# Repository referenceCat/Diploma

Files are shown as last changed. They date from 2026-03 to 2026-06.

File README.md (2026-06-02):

# Средства пользовательского ввода для лабораторного макета микроконтроллера

Выпускная квалификационная работа бакалавра

Студент: М.Ю. Буянов

Руководитель: к.т.н. П.Н. Бондаренко

Консультанты: А.А. Трусов, М.Н. Гречухин

# РЕФЕРАТ

МИКРОКОНТРОЛЛЕР, MIK32 АМУР, ЛАБОРАТОРНЫЙ МАКЕТ, ПОЛЬЗОВАТЕЛЬСКИЙ ВВОД, GPIO, ДРЕБЕЗГ КОНТАКТОВ, ПРОГРАММНАЯ ОБРАБОТКА СИГНАЛОВ.

В выпускной квалификационной работе рассматриваются аппаратные и программные средства пользовательского ввода, предназначенные для применения в учебном лабораторном макете на базе микроконтроллера MIK32 АМУР. Проводится анализ существующих отладочных плат и лабораторных стендов, формулируются требования к модулю ввода и обосновывается необходимость разработки отдельной платы с набором основных органов управления.

В работе разработаны схемотехнические и программные решения решения для подключения средств пользовательского ввода.

Результат работы - плата пользовательского ввода и программные примеры, которые могут использоваться при выполнении лабораторных работ по предмету “Микропроцессорные системы.”

# ABSTRACT

In the graduation work, hardware and software user input tools intended for use in an educational laboratory prototype based on the MIK32 AMUR microcontroller are considered. Existing development boards and laboratory stands are analyzed, requirements for the input module are formulated, and the need to develop a separate board with a set of basic controls is substantiated.

The work presents circuit and software solutions for connecting user input devices.

The result of the work is a user input board and software examples that can be used in laboratory assignments for the course “Microprocessor Systems.”

# СОДЕРЖАНИЕ

# ОПРЕДЕЛЕНИЯ, ОБОЗНАЧЕНИЯ И СОКРАЩЕНИЯ

CLK — тактовый сигнал, задающий моменты передачи данных в последовательном интерфейсе.

CS — сигнал выбора микросхемы или ведомого устройства на шине SPI.

GPIO — General Purpose Input/Output, — универсальные цифровые выводы ввода-вывода микроконтроллера.

I2C — последовательный двухпроводный интерфейс обмена данными между цифровыми устройствами.

JTAG — Joint Test Action Group, — интерфейс, применяемый для отладки и программирования микроконтроллеров.

MIK32 АМУР — отечественный 32-х битный МК от фирмы Микрон, построенный на архитектуре RISC-V.

MISO — линия интерфейса SPI, по которой ведомое устройство передает данные ведущему.

RC-цепь — электрическая цепь, состоящая из резистора и конденсатора и применяемая, в том числе, для сглаживания быстрых изменений сигнала.

RISC-V — открытая архитектура набора команд процессора.

SPI — Serial Peripheral Interface, — последовательный синхронный интерфейс обмена данными.

UART — Universal Asynchronous Receiver/Transmitter, — универсальный асинхронный приемопередатчик для последовательного обмена данными.

АЦП — аналого-цифровой преобразователь, периферийный блок МК, преобразующий входное аналоговое напряжение в цифровой код.

Лабораторный макет — учебное устройство или набор узлов, предназначенный для практического изучения работы микроконтроллера и его периферийных блоков.

МК — микроконтроллер, программируемая интегральная схема, содержащая процессорное ядро, память и периферийные блоки для управления внешними устройствами.

МКС — микроконтроллерная система.

Отладочная плата — плата с микроконтроллером, разъемами, цепями питания и средствами загрузки программы, предназначенная для разработки и проверки программного обеспечения.

ПО — программное обеспечение.

Пользовательский ввод — сигналы, формируемые человеком с помощью органов управления и передаваемые в МКС.

# ВВЕДЕНИЕ

Микроконтроллеры применяются в измерительной технике, промышленной автоматике, бытовых устройствах и средствах связи. При их изучении важно связывать программную часть с реальными электрическими сигналами. Студент должен не только написать программу, но и понять, как микроконтроллер взаимодействует с кнопками, датчиками, индикаторами и другими устройствами. Лабораторный макет дает для этого наглядную и воспроизводимую среду: позволяет подать входной сигнал, проверить его обработку программой и оценить работу периферийных блоков микроконтроллера.

Целевой платформой разрабатываемого лабораторного макета является отечественный МК MIK32 АМУР. Он построен на архитектуре RISC-V и может использоваться для разработки современных встраиваемых систем [1]. Для MIK32 доступны отладочные платы, однако готовых лабораторных макетов с развитым набором органов пользовательского ввода нет, а существующие примеры программного обеспечения охватывают не все распространенные сценарии.

Данная работа посвящена разработке средств пользовательского ввода как одной из частей лабораторного макета на базе MIK32 АМУР. Остальные узлы макета разрабатываются отдельно и будут объединены с модулем ввода в общем устройстве.

В настоящее время существует небольшое количество отладочных плат для MIK32, но все они содержат только минимальный набор встроенных органов управления, например одну или две кнопки и несколько светодиодов. Для выполнения лабораторных работ требуется подключать дополнительные модули и собирать схемы на макетной плате. Это увеличивает время подготовки, повышает вероятность ошибок подключения, способных привести к повреждению МК, и затрудняет повторяемость экспериментов, поэтому разработка средств пользовательского ввода для лабораторного макета на базе MIK32 АМУР является актуальной задачей.

Целью данной работы является разработка средств пользовательского ввода для лабораторного макета МК MIK32 АМУР.

# 1 Анализ существующих лабораторных макетов и постановка требований

Данный раздел посвящен постановке требований к блоку пользовательского ввода лабораторного макета. Рассматривается роль пользовательского ввода в учебных МКС, приводится классификация устройств ввода и формулируются требования к лабораторному макету. Далее анализируются особенности применения MIK32 АМУР, доступные отладочные платы на его основе, распространенные платы на других микроконтроллерах и готовые учебные стенды. По результатам сравнения обосновывается актуальность разработки собственного модуля ввода.

## 1.1 Роль лабораторного макета в обучении работе с МКС

Лабораторные макеты микроконтроллеров применяются для изучения принципов работы цифровых устройств, периферийных модулей и программного обеспечения встраиваемых систем. Лабораторный макет отличается от законченного устройства тем, что он предназначен не для выполнения заданной функции, а для изучения процессов, происходящих в схеме и программе. Поэтому учебный макет должен быть наглядным, иметь простую для понимания электрическую схему, обеспечивать доступ к основным сигналам и позволять изменять отдельные подключения.

Средства пользовательского ввода в таком макете выполняют несколько задач:

1. Формирование команд управления программой.

2. Задание режимов работы устройства.

3. Имитация внешних дискретных и аналоговых сигналов.

4. Отладка алгоритмов обработки событий пользователя.

К средствам ввода относятся кнопки, переключатели, потенциометры и различные датчики. Эти устройства позволяют микроконтроллеру получать информацию об окружающем мире.

При разработке необходимо учитывать не только удобство пользователя, но и ограничения аппаратной платформы. Модуль не должен занимать слишком много выводов микроконтроллера, обработка входных сигналов не должна занимать слишком много памяти и процессорного времени МК.

## 1.2 Классификация устройств пользовательского ввода

Устройства пользовательского ввода можно классифицировать по характеру формируемого сигнала и способу его обработки микроконтроллером. В микроконтроллерных системах наиболее распространены дискретные, аналоговые, импульсные. Также можно выделить интерфейсные устройства ввода — это устройства, которые относятся к первым 3 группам, но взаимодействуют с МК через один из популярных протоколов связи, например UART, I2C, SPI, а не напрямую. В учебном макете целесообразно использовать простые представители этих групп, так как они позволяют изучить базовые принципы обработки сигналов без лишней схемотехнической сложности.

Дискретные устройства формируют один из двух логических уровней. К ним относятся кнопки, переключатели, тумблеры, концевые выключатели, герконы и датчики с дискретным выходом. Было решено использовать в макете тактовые кнопки и рычажковые переключатели: кнопка формирует кратковременное событие, а переключатель задает устойчивое состояние. На этих элементах можно изучить считывание GPIO, обработку изменения уровня и подавление дребезга контактов. Рассматривалась возможность использовать группу штыревых разъемов с джампером, так как они надежнее переключателей, но джамперы могут легко потеряться при постоянном переключении и не так удобны в использовании.

При увеличении числа команд отдельные кнопки удобно объединять в клавиатурный блок. Если подключать каждую кнопку напрямую к отдельному выводу микроконтроллера, расход GPIO быстро становится слишком большим: например, для клавиатуры из 12 кнопок потребуется 12 входных линий без учета переключателей, энкодера и аналоговых регуляторов. Поэтому клавиатура отличается от простого набора кнопок не только конструктивным исполнением, но и способом организации считывания: несколько кнопок объединяются в общую схему и опрашиваются программно.

В работе используется клавиатура 4x3, содержащая 12 кнопок. На ее примере рассматривается задача считывания группы дискретных входов при ограниченном числе выводов микроконтроллера. Такая клавиатура может подключаться напрямую, матрицей строк и столбцов или через внешние регистры ввода. Сравнение этих вариантов позволяет выбрать схему, которая обеспечивает достаточное количество команд и при этом не занимает чрезмерное число GPIO.

Аналоговые устройства ввода формируют непрерывно изменяющееся напряжение, которое измеряется АЦП. К ним относятся потенциометры, аналоговые джойстики и датчики с аналоговым выходом. В работе в качестве базового аналогового элемента используется потенциометр, поскольку это одно из наиболее простых и понятных аналоговых устройств ввода.

Импульсные устройства ввода формируют последовательность переходов между логическими уровнями. К ним относятся механические, оптические и магнитные энкодеры, а также датчики с импульсным или квадратурным выходом. В работе используется механический поворотный энкодер. При его вращении формируются два связанных сигнала, по которым программа определяет направление и количество шагов. Такой элемент позволяет изучить обработку переходов, измерение временных характеристик сигнала и влияние частоты опроса на корректность распознавания.

Отдельную группу составляют интерфейсные устройства ввода, которые передают данные по SPI, I2C, UART или USB. К ним относятся клавиатурные контроллеры, сенсорные панели, цифровые джойстики, RFID-считыватели и датчики с цифровым выходом. Для учебного макета удобным примером является клавиатура с внешним контроллером или регистром ввода: ее состояние задается пользователем и легко проверяется визуально, поэтому обмен по цифровому интерфейсу можно изучать без дополнительного контроля внешней физической величины.

В данной работе основной акцент сделан на простых и наглядных устройствах ввода: кнопках, переключателях, клавиатуре, потенциометрах и поворотном энкодере. Такой выбор позволяет изучить основные типы сигналов, с которыми сталкивается микроконтроллер: логический уровень, аналоговое напряжение и импульсную последовательность. После освоения этих базовых случаев можно переходить к более сложным устройствам, так как они в большинстве случаев используют те же принципы.

## 1.3 Требования к лабораторному макету пользовательского ввода

Лабораторный макет пользовательского ввода должен быть пригоден для регулярного применения в учебном процессе. Поэтому к нему предъявляются требования, связанные с составом устройств, стоимостью, удобством эксплуатации, использованием ресурсов микроконтроллера и возможностью расширения.

Основные требования к такому макету можно сформулировать следующим образом:

Наличие основных типов устройств ввода. Макет должен содержать дискретные органы управления, аналоговые устройства, импульсное устройство ввода и интерфейсное устройство. Такой состав позволяет выполнять лабораторные работы по всем базовым видам пользовательского ввода. Навыки полученные в ходе выполнения ЛР позволят студентам работать с устройствами которые не представлены на макете.

Умеренная стоимость. Учебный макет должен быть доступен для изготовления в нескольких экземплярах, так как лабораторное оборудование обычно используется не одним студентом, а учебной группой.

Доступность элементной базы. При разработке необходимо использовать распространенные компоненты и избегать избыточно сложных узлов, если их функции можно показать на более простых элементах. Это упрощает изготовление, ремонт и повторение макета.

Экономное использование выводов микроконтроллера. В лабораторном макете выводы GPIO нужны не только для пользовательского ввода, но и для интерфейсов связи, отладки, индикации, измерений и подключения внешних модулей.

Удобство наблюдения и проверки сигналов. Основные линии ввода желательно вывести на контактные площадки или разъемы, к которым можно подключить осциллограф, логический анализатор или мультиметр.

Эргономика. Органы управления должны быть расположены так, чтобы студент мог быстро понять их назначение. Кнопки, переключатели, энкодер и аналоговые ручки должны иметь понятные обозначения, а их состояние должно легко считываться визуально.

Ремонтопригодность. В учебных условиях отдельные элементы могут выходить из строя из-за интенсивного использования, поэтому предпочтительно применять доступные компоненты и разборные соединения. Это позволяет заменить поврежденный элемент без переработки всей платы.

Таким образом, хороший лабораторный макет пользовательского ввода должен сочетать достаточный набор органов управления, низкую стоимость, экономное использование выводов, удобство измерений, надежность и понятную компоновку. Эти требования используются далее при анализе существующих плат и при разработке собственного модуля ввода.

## 1.4 MIK32 АМУР как целевая платформа учебного макета

В данной работе микроконтроллер MIK32 АМУР задан в качестве целевой аппаратной платформы лабораторного макета. Согласно техническому описанию, MIK32 АМУР является 32-разрядным микроконтроллером на архитектуре RISC-V [1].

На момент выполнения работы микроконтроллер доступен в 64-выводном корпусе QFN [2]. Часть выводов используется для питания, тактирования, отладки и интерфейсов связи, поэтому число линий, доступных для органов пользовательского ввода составляет 40 [1], поэтому при разработке макета необходимо экономно расходовать GPIO и предусматривать способы сокращения числа занятых выводов.

Схема ввода должна быть согласована с электрическими параметрами MIK32. Согласно информационному листу, напряжение питания микроконтроллера составляет 3,3 В ±10 % [2]. Цифровые устройства ввода должны формировать уровни, допустимые для входов микроконтроллера. Для аналоговых входов дополнительно учитывается диапазон входного сигнала АЦП: согласно техническому описанию, он составляет 0,015...Uref, где Uref находится в пределах 1,1...1,3 В и имеет номинальное значение 1,2 В [1]. Поэтому сигналы от потенциометров и других аналоговых источников должны быть ограничены до допустимого диапазона АЦП.

Для MIK32 доступно меньше готовых примеров программ, чем для более распространенных платформ, таких как Arduino или STM32. В частности, готовых примеров работы со сдвиговыми регистрами 74HC165 и поворотным энкодером для MIK32 найти не удалось. Поэтому программные алгоритмы опроса, фильтрации и преобразования входных состояний необходимо разрабатывать и проверять самостоятельно.

## 1.5 Обзор доступных отладочных плат на базе MIK32

На момент выполнения работы доступны несколько отладочных плат и модулей на базе MIK32. Они позволяют познакомиться с микроконтроллером, загрузить программу и подключить внешние устройства, однако их возможности с точки зрения готового пользовательского ввода ограничены.

DIP-MIK32 представляет собой компактный модуль с микроконтроллером MIK32, разъемами и минимальной необходимой обвязкой [4]. Такое исполнение удобно для прототипирования и установки на макетную плату. Однако развитых средств пользовательского ввода на нем нет: для выполнения лабораторных работ требуется собирать дополнительную схему. Стоимость DIP-MIK32 на странице заказа АО «Микрон» составляет 5 500 руб. [4]. Внешний вид платы представлен на рисунке 1.1.

Плата СТАРТ-MIK32 является более готовым решением для запуска программ, так как содержит внешнюю flash-память и программатор [4, 5]. Это облегчает первое знакомство с микроконтроллером и снижает порог входа при отладке программ. Тем не менее, с точки зрения лабораторных работ по пользовательскому вводу ее возможности также ограничены. Стоимость платы на странице заказа составляет 7 500 руб. [4].

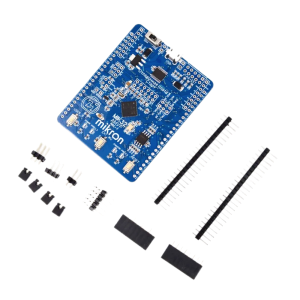
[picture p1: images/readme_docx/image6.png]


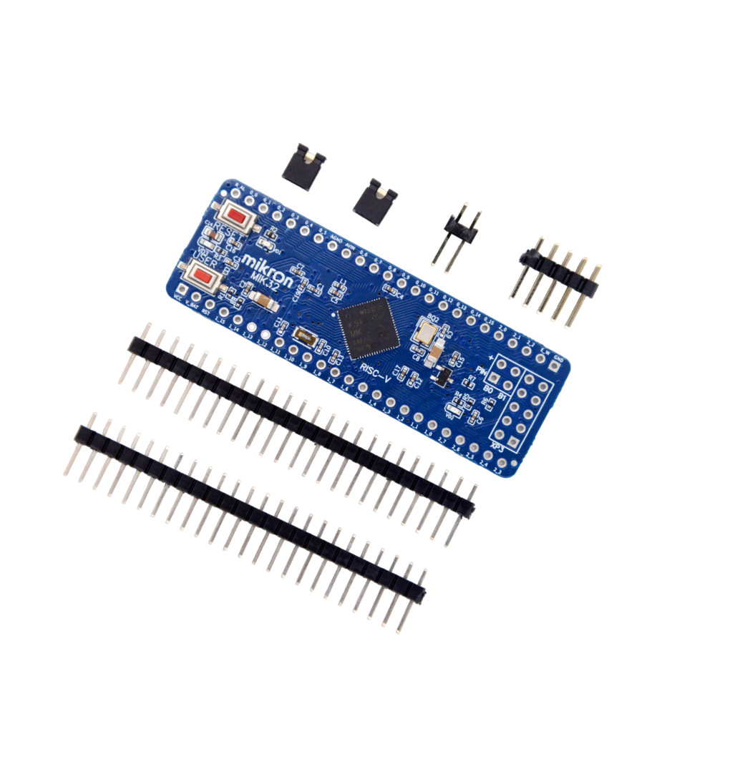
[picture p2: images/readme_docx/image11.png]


###### Рисунок 1.1 — Отладочные платы производства АО «Микрон» СТАРТ-MIK32 (слева) и DIP-MIK32 (справа)

Плата ELBEAR ACE-UNO выполнена в форм-факторе, близком к Arduino UNO, и может использоваться с Arduino-совместимыми модулями расширения [6]. Это делает ее удобной для экспериментов, так как многие периферийные устройства можно подключать через стандартные разъемы. Однако встроенных средств ввода на самой плате немного: пользовательская кнопка и светодиод. Стоимость платы в интернет-магазине Arduino54 составляет 8 400 руб. [6]. Внешний вид платы представлен на рисунке 1.2.

Плата RADIANT MIK32 также ориентирована на разработку и эксперименты с MIK32. В ее руководстве указаны пользовательские кнопки, светодиоды, Arduino UNO-совместимый разъем и выводы GPIO [7]. Это решение ближе к учебной отладочной плате, чем минимальные модули, однако и оно не содержит развитого набора органов управления. Для большинства лабораторных работ по пользовательскому вводу все равно потребуется отдельный модуль или внешняя макетная сборка. Стоимость составляет 9 060 руб. [7].

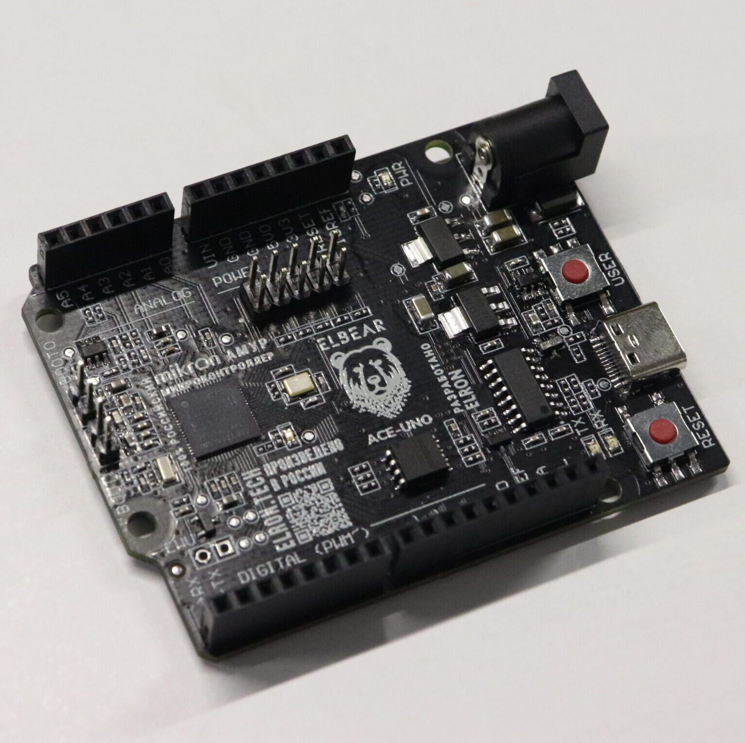
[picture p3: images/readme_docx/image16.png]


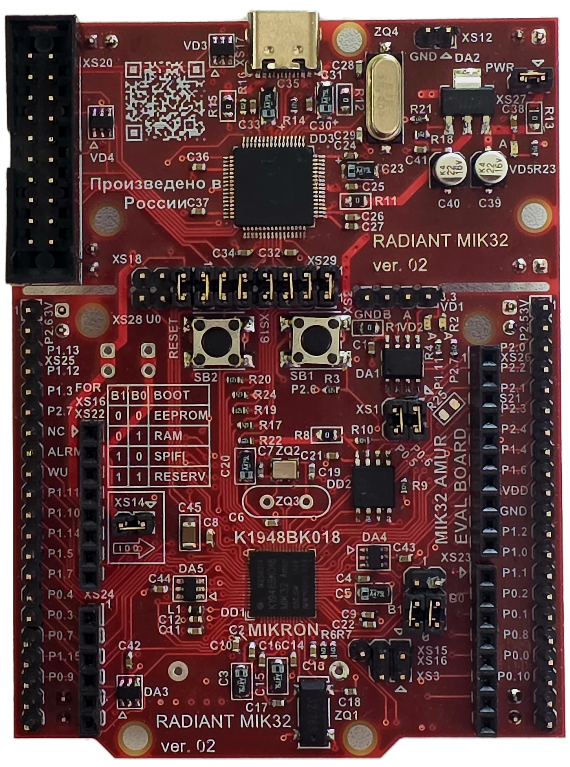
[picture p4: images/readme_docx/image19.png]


###### Рисунок 1.2 — Отладочные платы сторонних производителей ELBEAR ACE-UNO (слева) и RADIANT MIK32 (справа)

Следовательно, доступные платы на базе MIK32 решают задачу запуска и отладки программ, но не закрывают задачу готового лабораторного макета пользовательского ввода. Они предоставляют микроконтроллер и интерфейсы подключения, однако набор встроенных органов управления слишком мал для системного изучения устройств ввода. Одну из рассмотренных плат можно использовать как часть лабораторного макета. В этом случае не потребуется заново разрабатывать программатор, схему питания и минимальную обвязку микроконтроллера.

## 1.6 Сравнение с платами на других микроконтроллерах

Для оценки ситуации полезно сравнить платы MIK32 с распространенными решениями на других МК. Такие платы широко используются в обучении и прототипировании, поэтому они позволяют понять, какие подходы уже применяются в учебной практике.

Одним из самых дешевых решений является STM32F103C8T6 Blue Pill, изображенная на рисунке 1.3. Эта отладочная плата имеет большое количество выведенных контактов ввода-вывода и низкую стоимость: на странице магазина Амперо указана цена 249-299 руб. [8]. При этом встроенных средств пользовательского ввода на плате нет.

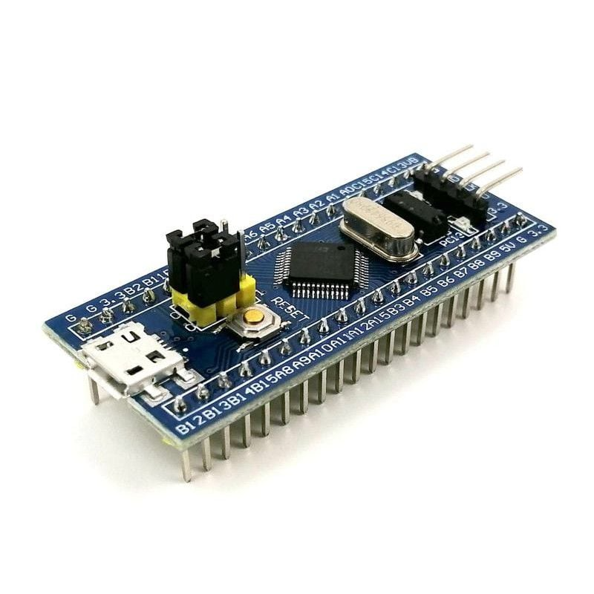
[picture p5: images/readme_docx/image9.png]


###### Рисунок 1.3 — Отладочная плата STM32F103C8T6 Blue Pill

Более удачным примером с точки зрения комплектации является Arduino Student Kit (рисунок 1.4). В него входит плата Arduino UNO, макетная плата, кнопки, потенциометры и другие компоненты для выполнения учебных заданий [9]. По составу комплект хорошо подходит для обучения, так как содержит не только микроконтроллерную плату, но и набор периферийных элементов. Однако схемы в нем необходимо каждый раз собирать на макетной плате.

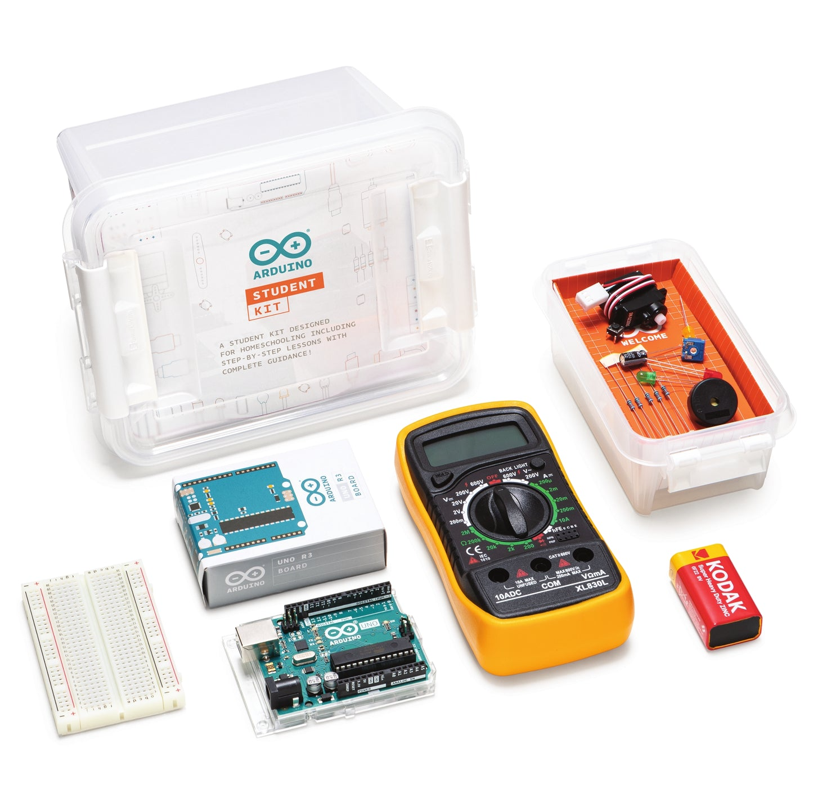
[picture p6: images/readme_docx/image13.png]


###### Рисунок 1.4 — Набор Arduino Student Kit

Хорошим примером завершенного учебного решения является MIKROE-701 UNI DS6 Development System. На странице поставщика она описана как универсальная отладочная плата, или лабораторный стенд, для изучения микроконтроллеров разных архитектур [10]. Плата содержит большое количество устройств ввода и вывода, гибкую систему коммутации, 12-разрядный внешний АЦП, температурный датчик, USB-UART мосты и разъемы для подключения внешних плат расширения. Цена платы на момент написания работы составляет 13 780 руб, что сопоставимо с ценой отладочных плат для MIK32. Такое решение хорошо показывает, каким должен быть учебный макет: студент получает готовую среду для экспериментов, а не набор отдельных элементов. При этом стенд не ориентирован на MIK32 и не может быть напрямую использован как решение задачи данной работы. Плата изображена на рисунке 1.5.

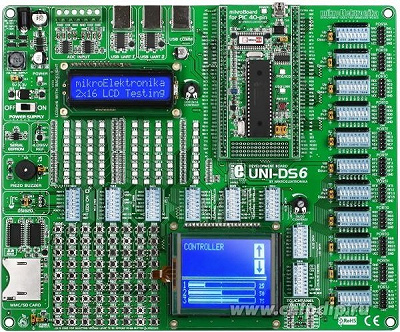
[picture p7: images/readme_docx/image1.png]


###### Рисунок 1.5 — MIKROE-701 UNI DS6

## 1.7 Сравнение с готовыми учебными лабораторными стендами

Отдельную группу решений составляют профессиональные учебные стенды для изучения микроконтроллеров. В отличие от обычных отладочных плат, такие стенды часто содержат набор тумблеров, кнопок, индикаторов, аналоговых датчиков, разъемов, клемм и методических материалов. Например, лабораторный стенд ЭЛБ-020.003.03 предназначен для изучения программирования микроконтроллеров и содержит элементы, необходимые для выполнения учебных работ [11], представлен на рисунке 1.6.

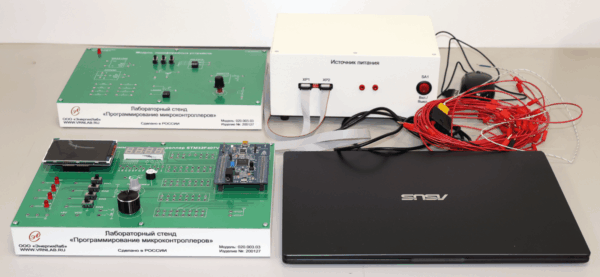
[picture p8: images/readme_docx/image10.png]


###### Рисунок 1.6 — Лабораторный стенд «Программирование микроконтроллеров» ЭЛБ-020.003.03

Преимущество таких стендов заключается в их завершенности. Студент работает с готовым оборудованием, где органы управления, индикация и измерительные точки уже размещены на панели и согласованы с учебной методикой. Это снижает количество ошибок подключения и делает лабораторные занятия более повторяемыми.

Основным недостатком готовых стендов является высокая стоимость. Например, цена стенда ЭЛБ-020.003.03 на странице поставщика составляет 392 824 руб. [11]. Такая стоимость существенно превышает стоимость большинства отладочных плат и делает стенд труднодоступным для небольших лабораторий, индивидуальной разработки и тиражирования в учебных группах. Кроме того, подобные стенды ориентированы на другие микроконтроллеры, например AVR или STM32, и не предназначены для работы с MIK32.

## 1.8 Сравнительный анализ решений

Сводное сравнение рассмотренных решений с точки зрения наличия различных устройств ввода приведено в таблице 1.1. В таблице указаны контроллеры, состав средств ввода, ориентировочная стоимость и вывод о применимости решения для задач данной работы. Стоимость приведена по открытым источникам на дату обращения и используется как ориентир для сравнения классов устройств.

Таблица 1.1 — Сравнение отладочных плат и лабораторных макетов

| Решение | Контроллер | Средства ввода | Ориентировочная стоимость | Вывод |
| --- | --- | --- | --- | --- |
| DIP-MIK32 | MIK32 АМУР | нет | 5 500 руб. [4] | Требуется внешний модуль ввода |
| СТАРТ-MIK32 | MIK32 АМУР | 1 кнопка | 7 500 руб. [4] | Требуется внешний модуль ввода |
| ELBEAR ACE-UNO | MIK32 АМУР | 1 кнопка | 8 400 руб. [6] | Требуется внешний модуль ввода |
| RADIANT MIK32 | MIK32 АМУР | 2 кнопки | 9 060 руб. [7] | Требуется внешний модуль ввода |
| Blue Pill | STM32F103 | нет | 249-299 руб. [8] | TI EK-TM4C123GXL LaunchPad |
| Arduino Student Kit | ATmega328P | 5 кнопок, 2 потенциометра 10 кОм, набор популярных датчиков | $79.75 [9], около 6000 руб. | Хорошая комплектация, но схемы нужно собирать |
| MIKROE-701 UNI DS6 | PIC, AVR, 8051, ARM, PSoC, dsPIC | десятки кнопок и рычажковых переключателей, внешний АЦП, датчик температуры | 13 780 руб. [10] | Хороший пример лабораторного макета, но не на MIK32 |
| ЭЛБ-020.003.03 | AVR | 8 тумблеров, 2 кнопки, внешний АЦП | 392 824 руб. [11] | Достаточный функционал, но очень высокая стоимость |

Из таблицы видно, что платы на базе MIK32 находятся в ценовом диапазоне, приемлемом для отладочных средств, однако они не содержат развитого набора пользовательского ввода. Платы на других микроконтроллерах демонстрируют ту же особенность: они удобны для программирования и подключения внешних модулей, но штатных кнопок, переключателей и аналоговых органов управления у них мало. Учебные комплекты и профессиональные стенды лучше подходят для лабораторной работы, однако они либо построены на другой аппаратной платформе, либо имеют высокую стоимость.

## 1.9 Актуальность работы и постановка задачи разработки

Проведенный анализ показывает, что задача разработки лабораторного макета для MIK32 АМУР в целом и средств пользовательского ввода для него в частности является актуальной, поскольку существующие решения не закрывают ряд требований, важных для учебного применения.

На рынке отсутствует доступный и функционально полный учебный макет на базе MIK32, ориентированный именно на изучение пользовательского ввода. Существующие платы позволяют познакомиться с микроконтроллером, но не предоставляют достаточного набора органов управления для проведения полноценных лабораторных работ.

В доступных платах на базе MIK32 отсутствует развитый набор средств пользовательского ввода. DIP-MIK32, СТАРТ-MIK32, ELBEAR ACE-UNO и RADIANT MIK32 подходят для запуска и отладки программ, но в них мало встроенных кнопок, переключателей и аналоговых регуляторов. Для учебного макета этого недостаточно, так как студенту необходимо изучать не один отдельный вход, а несколько типов пользовательского воздействия: дискретные сигналы, клавиатурный ввод, аналоговое напряжение и импульсные сигналы энкодера.

Сравнение с другими платами и стендами показывает разрыв между дешевыми отладочными платами и дорогими профессиональными учебными стендами. Недорогие платы имеют мало встроенных средств ввода, а функционально богатые стенды стоят значительно дороже. Решение на подобие MIKROE-701 UNI DS6 будет оптимальным с точки зрения соотношения цены и практичности.

Для MIK32 доступно меньше готовых примеров программ, чем для более распространенных платформ, таких как Arduino или STM32. Это означает, что для лабораторного макета недостаточно разработать только аппаратную часть. Необходимо также подготовить алгоритмы опроса кнопок и переключателей, обработки клавиатуры, определения направления вращения энкодера и считывания аналоговых значений. Без такой программной части макет будет менее полезен в учебном процессе.

Таким образом, актуальность работы определяется тем, что в существующих продуктах отсутствует сочетание свойств, необходимых для учебного макета на базе MIK32: отечественный микроконтроллер, развитый набор устройств пользовательского ввода, умеренная стоимость, возможность отключения отдельных блоков, удобство измерений и наличие программных примеров для лабораторных работ.

В связи с этим в работе ставится задача разработки средств пользовательского ввода для лабораторного макета микроконтроллера MIK32 АМУР. Разрабатываемое решение должно включать аппаратную часть, обеспечивающую подключение кнопок, переключателей, клавиатуры, энкодера и аналоговых регуляторов, а также программные примеры для их опроса и обработки. В следующих разделах рассматриваются схемотехнические варианты подключения устройств ввода, особенности их программной обработки и проверка работоспособности разработанного решения.

# 2 Разработка дискретных средств ввода

Данный раздел посвящен разработке дискретных средств пользовательского ввода, предназначенных для формирования логических сигналов, обрабатываемых микроконтроллером. Рассматриваются требования к кнопкам и переключателям, способы подключения клавиатуры 4x3, методы расширения числа входов и алгоритмы программной обработки дискретных сигналов.

## 2.1 Требования к дискретным устройствам ввода

Дискретные устройства ввода предназначены для формирования логических сигналов, по которым программа микроконтроллера определяет действия пользователя. В разрабатываемом лабораторном макете используются два типа таких устройств: тактовые кнопки для кратковременных команд и рычажковые переключатели для задания устойчивых состояний. Для макета требуется подключить 12 кнопок, например цифры от 0 до 9, ВВОД и ОТМЕНА, которые можно рассматривать как клавиатуру 4x3, и 8 рычажковых переключателей.

Для макета принято решение использовать рычажковые переключатели как наиболее простые дискретные устройства ввода. Их состояние можно считать непосредственно из регистра GPIO без настройки внешнего интерфейса и сложной схемы опроса. Это удобно для начальных лабораторных работ, где необходимо показать связь между положением элемента управления и логическим уровнем на входе микроконтроллера.

Для большого количества кнопок используется клавиатура 4x3. В отличие от отдельных переключателей, клавиатура содержит группу однотипных кнопок, число которых в дальнейшем может быть увеличено, например при переходе к клавиатуре 4x4 или панели функциональных клавиш. Поэтому способ подключения клавиатуры должен сохранять общий принцип считывания группы кнопок и по возможности не приводить к пропорциональному росту числа занятых выводов микроконтроллера.

При выборе способа подключения необходимо учитывать временные характеристики пользовательского ввода и минимизировать расход ресурсов контроллера, в первую очередь количество занятых GPIO.

## 2.2 Временные параметры опроса кнопок и переключателей

Для определения временных параметров пользовательского воздействия была проведена серия из 10 экспериментов с быстрым нажатием кнопки и переключением переключателя. [12] В макете используются переключатели DIP Switch 2.54 mm Regular Type производства CONNFLY [13] и тактовые кнопки серии KLS7-TS6601 6x6 [14]. По результатам измерений наименьшая продолжительность нажатия составила около 40 мс, продолжительность отпускания тоже около 40 мс. Для переключателей минимальная длительность одного состояния около 300 мс.

Эти значения рассматриваются как предельные условия работы, полученные при намеренно быстром нажатии на кнопку; при обычной эксплуатации лабораторного макета такие режимы, как правило, достигаться не будут.

Длительность дребезга кнопки, использованной в макете, не превысила 1 мс и, как правило, составляла около 50 мкс, как видно на осциллограмме на рисунке 2.1. На рисунке ниже приведена осциллограмма дребезга данной модели кнопки. Для рычажковых переключателей длительность дребезга не превысила 5 мс.

Продолжительность состояния и дребезга кнопок и переключателей приведена в диаграмме на рисунке 2.2.

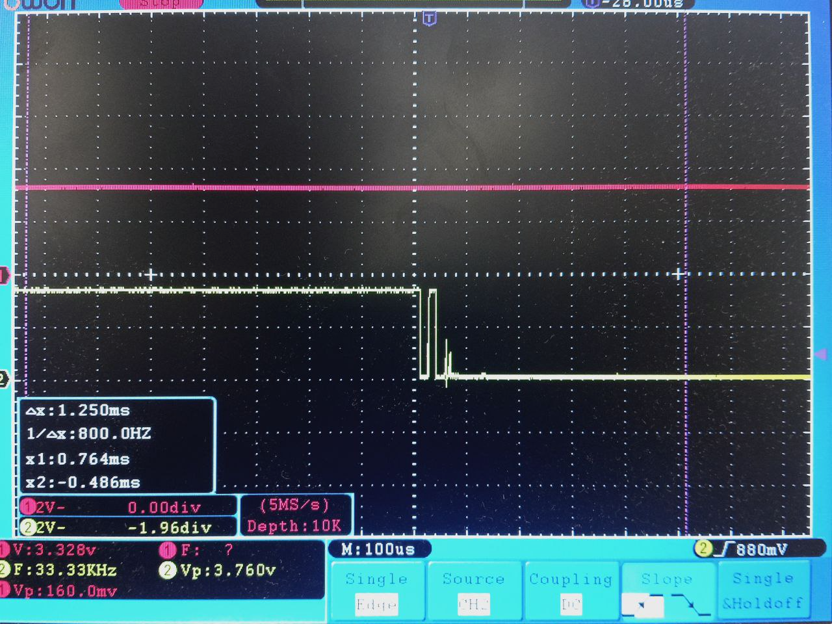
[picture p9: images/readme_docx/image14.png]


###### Рисунок 2.1 — Один из тестов длительности дребезга кнопки. Кнопка подключена ко второму каналу осциллографа

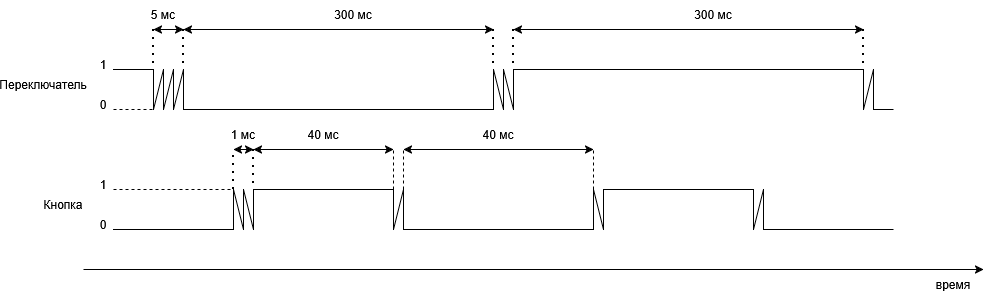
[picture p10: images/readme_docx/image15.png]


###### Рисунок 2.2 — Временные характеристики нажатия кнопки и переключателя: максимальная длительность дребезга, минимальная продолжительность состояний "0" и "1"

На основании этих измерений система опроса должна иметь запас и надежно регистрировать нажатия длительностью не менее 40 мс. Алгоритм обработки должен определять текущее состояние и его смену, подавлять дребезг контактов, при условии что будет выбран аппаратный способ борьбы с дребезгом, и сохранять возможность обработки нескольких входов в пределах одного цикла опроса. Период опроса должен быть выбран так, чтобы программа успевала обнаруживать самые быстрые действия пользователя и при этом не тратила лишние вычислительные ресурсы.

Для лабораторного макета важно сохранить компромисс между надежностью и отзывчивостью. Слишком малое время фильтрации может пропускать дребезг и приводить к ложным срабатываниям, а слишком большое - ухудшать реакцию на быстрые нажатия.

Период опроса должен быть в несколько раз меньше длительности одного состояния, например 10 мс для кнопок и 70 мс для переключателей, так в худшем случае на одно состояние придется 3 опроса. При этом итоговая задержка реакции складывается из периода опроса и выбранного времени фильтрации.

## 2.3 Подключение рычажковых переключателей

Рычажковый переключатель задает устойчивое логическое состояние, которое сохраняется после воздействия пользователя. Поэтому он подходит для выбора режима работы, задания начальных условий программы или имитации простого датчика с дискретным выходом. В разрабатываемом макете используется 8 рычажковых переключателей, подключенных напрямую к выводам GPIO микроконтроллера. Каждый переключатель остается независимым входом, поэтому его состояние можно считывать как при периодическом опросе, так и при обработке прерывания по изменению уровня.

Дискретные входы должны быть согласованы с логическими уровнями МИК32 АМУР. Согласно информационному листу микроконтроллера, напряжение питания составляет 3,3 В ±10 % [2], то есть допустимый диапазон питания основного домена составляет 2,97-3,63 В. В проектируемой схеме логический «0» должен формироваться уровнем, близким к GND, а логическая «1» - уровнем, близким к VCC 3,3 В. Подача на входы сигналов уровня 5 В не допускается.

При прямом подключении один контакт переключателя соединяется с линией питания, а второй подключается к входу микроконтроллера. Чтобы вход не оставался в неопределенном состоянии, используется подтягивающий резистор. В выбранной схеме подтяжка выполнена к земле: при разомкнутом контакте на входе формируется логический «0», а при замыкании переключателя вход соединяется с питанием и формируется логическая «1». Подтяжка реализована внешним резистором для каждого переключателя. Схема подключения представлена на рисунке 2.3.

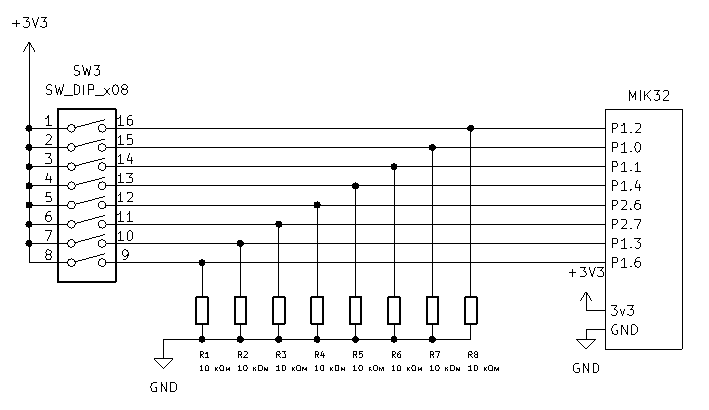
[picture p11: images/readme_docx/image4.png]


Рисунок 2.3 — Схема подключения рычажковых переключателей

Для определения состояния переключателя достаточно настроить нужный вход МК на вход и прочитать бит из соответствующего регистра. Фрагмент примера из приложения А:

GPIO_1->DIRECTION_IN = GPIO_PIN_2;

uint8_t lever_state = (GPIO_1->STATE & GPIO_PIN_2) != 0;

При изменении положения контакты переключателя не переходят из одного состояния в другое мгновенно. Как и у кнопок, у них возникает дребезг контактов, из-за которого микроконтроллер может зафиксировать несколько быстрых изменений уровня вместо одного переключения. Вопрос подавления дребезга рассматривается далее в отдельном подразделе.

## 2.4 Подключение клавиатуры 4x3 напрямую

Самый простой способ заключается в соединении каждой кнопки с отдельным входом микроконтроллера. В этом случае 12 кнопок требуют 12 GPIO. Один контакт кнопки подключается к линии питания, а второй - к входу микроконтроллера, аналогично с переключателями в подраздела 2.3. Прямое подключение клавиатуры 4x3 рассматривается как базовый вариант, с которым далее сравниваются другие способы подключения.

Преимущество прямого подключения заключается в простоте схемы и программы. Состояние каждой кнопки можно считать напрямую из регистра GPIO, а обработка нажатий сводится к сравнению текущего и предыдущего состояния входа. При таком подходе легко поддерживать одновременные нажатия, поскольку каждая кнопка имеет собственный входной канал. Кроме того, прямое подключение позволяет использовать внешние прерывания GPIO для реакции на изменение состояния кнопки без постоянного циклического опроса всех входов. Можно добавить аппаратное средство борьбы с дребезгом.

Программный код для прямого подключения клавиатуры аналогичен коду для рычажковых переключателей: для каждой кнопки настраивается вход GPIO, после чего программа считывает соответствующий бит регистра состояния порта. Отличие состоит только в количестве входов.

Недостаток прямого подключения состоит в большом расходе выводов микроконтроллера. Только клавиатура 4x3 занимает 12 GPIO, а с учетом 8 рычажковых переключателей суммарно требуется уже 20 цифровых входов, не считая энкодера, аналоговых ручек и других сигналов макета. Для лабораторного стенда выводы микроконтроллера являются одним из наиболее ценных ресурсов. Поэтому прямое подключение не является оптимальным решением для итоговой платы.

## 2.5 Подключение клавиатуры 4x3 матрицей

Матричное подключение уменьшает число занятых выводов за счет объединения кнопок в строки и столбцы. Для клавиатуры 4x3 требуется 7 линий: 4 строки и 3 столбца. При сканировании программа поочередно активирует строки и считывает состояние столбцов. Если при активной строке на одном из столбцов обнаруживается изменение уровня, программа определяет нажатую кнопку по номеру строки и столбца.

По сравнению с прямым подключением матрица позволяет сэкономить 5 выводов микроконтроллера: вместо 12 GPIO используются 7. Однако такая схема требует более сложного алгоритма опроса. Необходимо последовательно переключать строки, выдерживать время установления уровней и выполнять чтение столбцов для каждой строки. Период полного опроса клавиатуры зависит от числа строк и задержек в алгоритме сканирования. В отличие от прямого подключения, матрица не позволяет назначить независимое прерывание на каждую кнопку. Алгоритм сканирования матрицы включает несколько этапов:

Перевести одну строку в активное состояние.

Выдержать небольшую задержку для установления уровней.

Считать уровни на линиях столбцов.

Определить нажатые кнопки для текущей строки.

Повторить действия для остальных строк.

Дополнительная проблема матричной клавиатуры возникает при одновременном нажатии нескольких кнопок. В некоторых сочетаниях возможно появление фантомных срабатываний, когда программа определяет нажатой кнопку, которая фактически не нажималась. Для устранения этой проблемы применяют диоды [15], включенные последовательно с кнопками, но это увеличивает количество компонентов и усложняет монтаж: для клавиатуры 4x3 требуется 12 диодов и 3 резистора. Схема подключения клавиатуры 4х4 изображена на рисунке 2.4, для клавиатуры 4х3 схема аналогична за исключением отсутствия левого столбца кнопок.

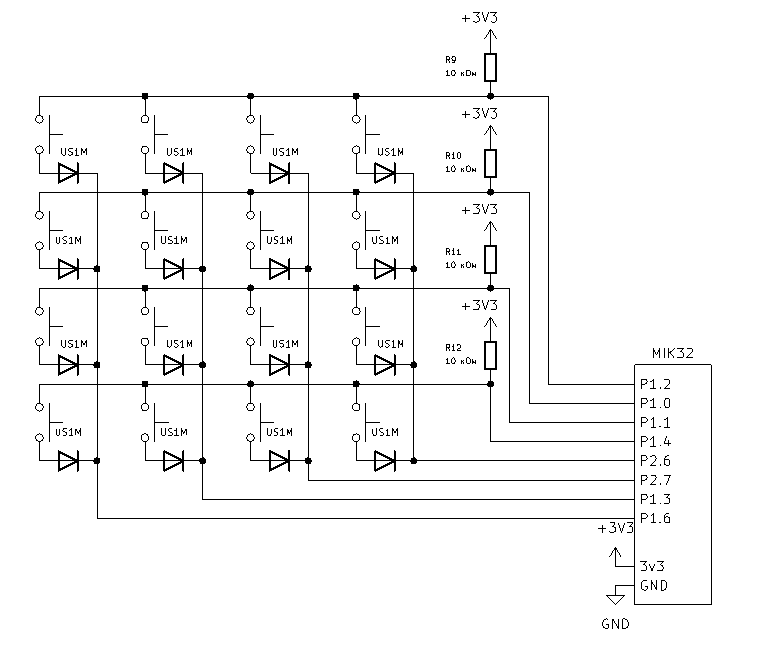
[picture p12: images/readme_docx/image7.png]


###### Рисунок 2.4 — Схема подключения клавиатуры 4 на 4

Матричное подключение экономит GPIO, но добавляет схемотехнические и усложняет ПО.

## 2.6 Подключение кнопок через сдвиговые регистры 74HC165

Третий вариант заключается в подключении кнопок к параллельным входам сдвигового регистра, например 74HC165. 74HC165 является распространенным решением: микросхема выпускается разными производителями и представлена в каталогах поставщиков в значительных количествах [16-18]. Один 74HC165 имеет 8 параллельных входов, поэтому для 12 кнопок достаточно двух микросхем. Оставшиеся входы могут быть зарезервированы для дальнейшего расширения, например для кнопки на ручке энкодера. Подключение 74HC165 занимает 3 выхода МК [12].

При работе с 74HC165 микроконтроллер сначала формирует сигнал загрузки параллельных входов, после чего последовательно считывает биты состояния. Несколько микросхем можно каскадировать: последовательный выход одной микросхемы подключается к последовательному входу следующей, и вся цепочка считывается как один более длинный сдвиговый регистр. Это делает решение хорошо расширяемым: увеличение числа кнопок требует добавления микросхемы, но почти не увеличивает число линий микроконтроллера. Недостатком такого подхода является невозможность получить отдельное прерывание от каждой кнопки: микроконтроллер видит не отдельные входы, а последовательный поток данных, поэтому состояние кнопок определяется периодическим считыванием регистра.

Считывание 74HC165 можно выполнить двумя способами. Первый способ - программное управление линиями GPIO. В этом случае тактовые импульсы формируются средствами программы, а данные считываются по одному биту после каждого импульса. Такой подход не требует настройки аппаратного SPI, но расходует процессорное время и делает обмен зависимым от задержек в программе.

Второй способ - подключение 74HC165 к аппаратному интерфейсу SPI. В этом случае тактовый сигнал формируется периферийным блоком SPI, а данные считываются через вход MISO. Дополнительная линия GPIO используется для загрузки параллельного состояния в регистр. Такой вариант уменьшает программную нагрузку, используя стандартную периферию микроконтроллера.

Готовых примеров работы с 74HC165 для MIK32 найти не удалось, поэтому для макета был написан собственный драйвер. Он формирует сигнал загрузки состояний кнопок, считывает данные по SPI и преобразует полученное значение в битовую маску. При проверке аппаратного SPI на MIK32 были обнаружены две практические особенности: сигнал CS инвертирован, поэтому им приходится управлять вручную, а линия CLK после завершения обмена не сразу возвращается к нулю и устанавливается в низкий уровень только через несколько миллисекунд. Эти особенности не нарушили целостность считывания, но были учтены при настройке обмена и отладке программы.

Штатный способ расширения числа входов - каскадирование регистров, при котором последовательный выход Q7 одного регистра подключается к последовательному входу DS следующего; такая возможность прямо указана в описании 74HC165 [18]. Если необходимо подключить к той же SPI-шине другие устройства, нужно обеспечить, чтобы в каждый момент времени линию MISO формировало только одно устройство. Это важно при совместном использовании выбранной SPI-шины несколькими внешними устройствами. Для обычных SPI-устройств это выполняется сигналом CS, переводящим невыбранное устройство в высокоимпедансное состояние. Для 74HC165 такой функции нет, поэтому возможны несколько решений: подключить выход цепочки 74HC165 к MISO через внешний буфер с третьим состоянием, например 74HC125, использовать отдельную линию MISO/отдельный SPI-интерфейс для регистров или включить последовательный резистор 1 кОм между выходом Q7 последнего 74HC165 и общей линией MISO. В работе был протестирован 3 вариант, в качестве второго ведомого устройства выступала плата Arduino Leonardo, посылающая возрастающие байты при подаче логической “1” на входе CS. Схема подключения представлена на рисунке 2.5

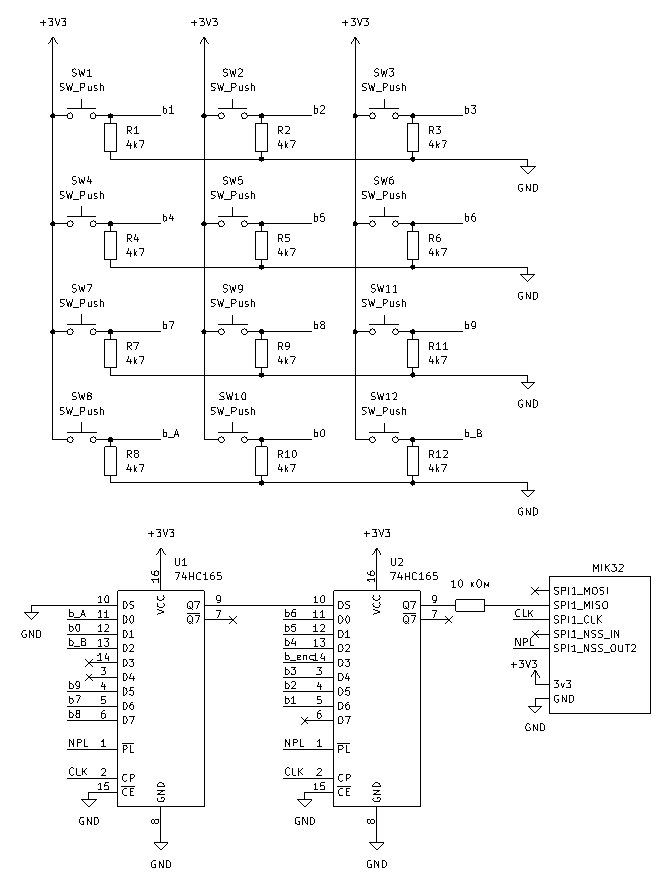
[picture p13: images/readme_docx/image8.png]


###### Рисунок 2.5 — Схема подключения клавиатуры,через регистр 74HC165

## 2.7 Сравнение способов подключения клавиатуры 4x3

Для выбора схемы подключения были рассмотрены три варианта: прямое подключение кнопок к GPIO, матричная клавиатура 4x3 и подключение через сдвиговые регистры 74HC165. Основным критерием выбора стало количество занятых выводов микроконтроллера, поскольку GPIO являются наиболее ограниченным ресурсом лабораторного макета.

При выборе способа построения модуля пользовательского ввода необходимо учитывать не только работоспособность отдельной схемы, но и ее пригодность для всего лабораторного макета. Один и тот же набор органов управления может быть подключен разными способами, каждый из которых имеет преимущества и ограничения. Для сравнения вариантов используются следующие критерии:

количество занятых выводов микроконтроллера;

затрачиваемая память МК

сложность программного алгоритма;

возможность обработки одновременных действий пользователя;

стоимость и доступность компонентов;

возможность дальнейшего расширения;

Затраты памяти для рассмотренных вариантов имеют один порядок, поскольку во всех случаях программа хранит текущее состояние кнопок, предыдущее состояние и служебные данные для фильтрации дребезга.

Стоимость также имеет один порядок, 100-200 рублей, это несравнимо ниже цены отладочной платы и не окажет заметного эффекта на итоговую стоимость макета. Отличия подходов описаны в таблице 2.1

Таблица 2.1 — Сравнение подходов подключения клавиатуры к МК

| Способ подключения | GPIO для 12 кнопок | Дополнительные компоненты | Программная сложность | Масштабирование |
| --- | --- | --- | --- | --- |
| Прямое подключение | 12 | 12 резисторов 10 кОм | низкая | плохое, каждая новая кнопка требует GPIO |
| Матрица 4x3 | 7 | 3 резистора 10 кОм, 12 диодов | низкая | среднее, кол-во выходов для матрицы M на N составляет M+N |

Продолжение таблицы 2.1

| каскад 74HC165 | 3 | 2 74HC165, 12 резисторов 10 кОм | средняя | хорошее, добавление входов каскадированием |
| --- | --- | --- | --- | --- |

При прямом подключении клавиатура 4x3 занимает 12 выводов. Этот вариант имеет минимальную программную и аппаратную сложность, но плохо масштабируется. При добавлении 8 рычажковых переключателей расход GPIO становится слишком большим.

Матричное подключение уменьшает число линий до 7, что заметно лучше прямого варианта. Допустимый вариант для макета.

Подключение через 74HC165 требует минимального числа дополнительных линий микроконтроллера и хорошо расширяется каскадированием микросхем, но программная и аппаратная реализация сложнее, чем другие варианты.

Для итоговой реализации выбран вариант подключения кнопок через сдвиговые регистры 74HC165 с чтением данных по SPI. Такое решение обеспечивает приемлемую сложность схемы, экономит выводы микроконтроллера и хорошо масштабируется, а также позволяет изучить работу с интерфейсами связи.

## 2.8 Дребезг контактов кнопок и переключателей

Механические кнопки и рычажковые переключатели не формируют идеальный одиночный переход между логическими уровнями. При замыкании и размыкании контактов возникает дребезг: в течение короткого времени вход микроконтроллера может несколько раз переключаться между «0» и «1». Если не учитывать этот эффект, одно нажатие кнопки может быть ошибочно обработано как несколько нажатий, а изменение положения переключателя - как серия быстрых переключений. В разделе 2.2 были получены значения длительности дребезга: для кнопки до 1 мс, для рычажковых переключателей до 5 мс.

В работе были рассмотрены и проверены три варианта защиты от дребезга: специализированная микросхема MC14490, RC-фильтр и программная фильтрация. Эти варианты отличаются числом дополнительных компонентов, задержкой, стоимостью и влиянием на программную часть.

MC14490 является специализированной микросхемой подавления дребезга. Она удобна тем, что не требует отдельной программной обработки и не занимает дополнительные выводы микроконтроллера для каждого канала. Одна микросхема содержит 6 каналов, поэтому для 8 переключателей потребовались бы две микросхемы, а для переключателей и кнопок 4 микросхемы. Схема подключение переключателей приведена на рисунке 2.6.

RC-фильтр является простым аппаратным способом сглаживания дребезга [19]. Он дешев и может быть собран из распространенных компонентов, однако для большого количества входов требует значительного числа элементов. Для каждого канала необходимы как минимум резистивно-емкостная цепь и желательно формирователь с четким порогом переключения, например вход с триггером Шмитта [19]. На печатной плате такое решение может быть приемлемым, но при макетировании оно усложняет монтаж и увеличивает вероятность ошибок соединения.

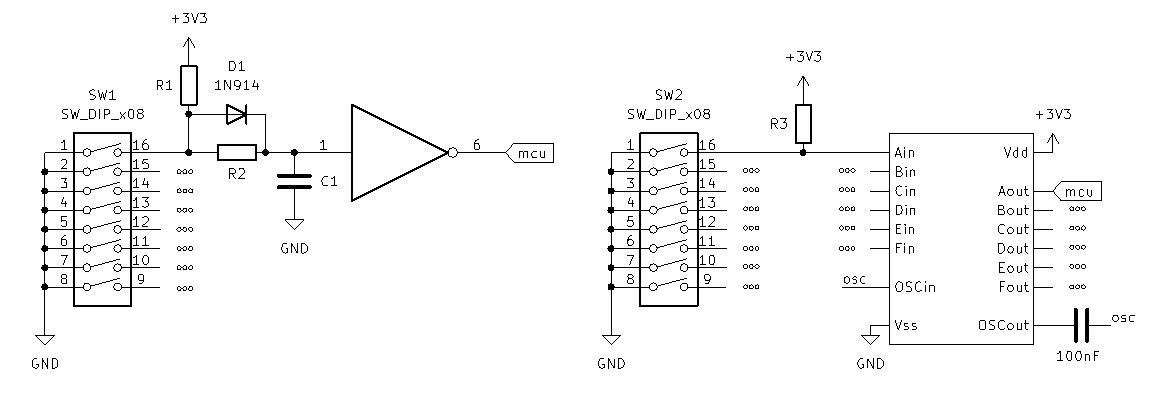
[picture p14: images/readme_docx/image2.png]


###### Рисунок 2.6 — Схемы аппаратного подавления дребезга контактов

Программная фильтрация не требует дополнительных компонентов и позволяет изменять параметры подавления дребезга без переделки схемы. Суть метода состоит в том, что изменение состояния входа принимается не сразу, а только после того, как новое значение сохраняется в течение заданного времени или подтверждается несколькими последовательными измерениями. Сравнение способов подавления дребезга для блока из 8 переключателей приведено в таблице 2.2.

Таблица 2.2 — Сравнение способов подавления дребезга контактов

| Способ | Примерная цена | Доступность | Сложность монтажа | Сложность программирования |
| --- | --- | --- | --- | --- |
| MC14490 | ~300 руб | низкая, срок доставки около 6 недель | средняя | низкая |
| RC-фильтр | ~500 руб | высокая | высокая | низкая |
| Программная фильтрация | - | - | - | средняя |

По результатам проверки для макета выбрана программная защита от дребезга. Она не увеличивает стоимость и сложность платы, не требует дополнительных микросхем и позволяет подобрать время фильтрации с учетом измеренных условий работы. Такой вариант удобен для лабораторного макета, где важно иметь возможность изменять алгоритм обработки и сравнивать разные параметры фильтрации программно.

## 2.9 Программная обработка кнопок и переключателей

Программная обработка дискретных входов выполняется в несколько этапов. Сначала микроконтроллер получает сырые состояния входов: для кнопок они считываются из цепочки 74HC165 по SPI, а для рычажковых переключателей - непосредственно из регистров GPIO. Затем программа сравнивает новое состояние с предыдущим и определяет события: нажатие, отпускание или изменение положения переключателя.

Для защиты от дребезга используется программная фильтрация по времени. При первом обнаружении изменения входа программа не принимает его немедленно, а запускает проверку стабильности. Новое состояние считается действительным только после того, как оно сохраняется без изменений в течение заданного интервала. Такой алгоритм позволяет отделить реальное действие пользователя от кратковременных колебаний контактов.

В итоговой реализации для рычажковых переключателей используется опрос с периодом 30 мс. Переключение фиксируется только в том случае, если новое состояние сохраняется при следующем опросе. Для кнопок, подключенных через 74HC165, применяется более короткий интервал подтверждения: состояние кнопки принимается только при сохранении в течение 10 мс. Такие параметры согласуются с измеренной длительностью дребезга и не создают заметной задержки при обычной работе пользователя.

Для кнопок, подключенных через 74HC165, фильтрация естественно совмещается с периодическим опросом регистров. Для каждого входа хранится сырое состояние, подтвержденное состояние и время последнего изменения. Для рычажковых переключателей, подключенных напрямую к GPIO, возможны два режима: периодический опрос или прерывание по изменению уровня с последующей программной проверкой состояния после интервала подавления дребезга.

# 3 Разработка аналоговых и импульсных средств ввода

Данный раздел посвящен разработке аналоговых и импульсных средств пользовательского ввода. Рассматриваются подключение поворотного энкодера и аналоговых ручек вращения, а также особенности программной обработки сигналов АЦП и импульсных последовательностей.

## 3.1 Назначение поворотных органов управления

Поворотные органы управления применяются в лабораторных макетах для задания числовых параметров, выбора режимов работы и демонстрации обработки изменяющихся входных сигналов. В данной работе рассматриваются два типа таких устройств: инкрементальный поворотный энкодер и аналоговые ручки вращения на основе потенциометров.

Аналоговая ручка вращения, выполненная на потенциометре, формирует абсолютное значение. Ее положение соответствует определенному уровню напряжения, который считывается микроконтроллером с помощью АЦП. Такой ввод удобен для задания уровня, коэффициента, порога срабатывания или другого параметра, который должен изменяться плавно.

Работа с потенциометром в ходе ЛР позволит студентам изучить взаимодействие с АЦП и обработку аналоговых сигналов.

Энкодер используется для ввода относительного изменения положения. В отличие от потенциометра, механический инкрементальный энкодер не задает абсолютное напряжение. При вращении он формирует последовательность импульсов, по которым программа определяет количество шагов и направление вращения. Такой орган управления удобен для изменения числовых параметров, выбора пунктов меню и работы с величинами, которые могут увеличиваться или уменьшаться без ограничения полного угла поворота. Получение данных с энкодера требует соблюдение строгих требований к частоте опроса и длительности обработки результата в ПО.

## 3.2 Подключение поворотного энкодера

На начальном этапе предполагалось сравнить несколько модулей поворотных энкодеров. Однако модуль KY-040 на основе механического инкрементального энкодера серии EC11 после первичной проверки удовлетворил требованиям макета, поэтому дальнейшее сравнение модулей не потребовалось. KY-040 является распространенным и недорогим модулем, представлен в продаже как готовый модуль с ручкой [20, 21]. Типовой механический инкрементальный энкодер имеет два сигнальных канала A и B. Сигналы этих каналов сдвинуты по фазе. Если при вращении сначала изменяется канал A, а затем канал B, программа определяет одно направление. Если порядок изменений обратный, определяется противоположное направление. Такой способ называется квадратурным кодированием.

Каналы A и B подключаются к цифровым входам микроконтроллера, следует использовать входы P0.11 и P0.12, так как они являются входом 16-битного таймера MIK32, который имеет режим декодирования [1]. Как и для кнопок, входы не должны оставаться в неопределенном состоянии, поэтому применяются подтягивающие резисторы к питанию. Модуль KY-040 уже содержит элементы аппаратной фильтрации сигналов энкодера, что упрощает подключение к входам микроконтроллера. На этапе разработки модуль установлен целиком; в дальнейшем его компоненты решения могут быть перенесены непосредственно на общую лабораторную плату. При вращении энкодера механические контакты поочередно замыкаются и размыкаются, формируя последовательность логических уровней. Энкодер имеет встроенную кнопку, она подключается как часть клавиатуры из 2. Схема подключения представлена на рисунке 3.1.

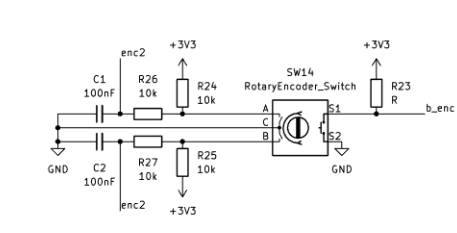
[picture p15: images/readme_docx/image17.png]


###### Рисунок 3.1 — Схема подключения энкодера

Энкодер удобен для лабораторного макета тем, что позволяет демонстрировать сразу несколько задач: считывание двух цифровых входов, анализ последовательности переходов, обработку внешних событий, работу с прерываниями или таймером в режиме декодирования или захвата.

## 3.3 Алгоритм обработки энкодера

Для обработки энкодера программа хранит предыдущее состояние каналов A и B и сравнивает его с текущим. Каждое состояние можно представить двумя битами. При нормальном вращении состояния изменяются в определенной последовательности, а направление определяется порядком переходов.

Готовый драйвер энкодера для MIK32 найти не удалось, поэтому обработка входного сигнала реализована самостоятельно. Пример программы считывает два цифровых входа, определяет допустимость перехода между состояниями и изменяет счетчик положения в зависимости от направления вращения.

Общий алгоритм обработки энкодера включает следующие шаги:

Считать текущие уровни каналов A и B.

Сформировать двухбитное состояние энкодера.

Сравнить текущее состояние с предыдущим.

Определить, соответствует ли переход допустимому шагу вращения.

Увеличить или уменьшить счетчик положения в зависимости от направления.

Отбросить некорректные переходы, связанные с дребезгом, пропуском импульса или слишком быстрым вращением.

Допустимые переходы соответствуют повороту на один шаг. Если переход невозможен для нормальной квадратурной последовательности, он может быть связан с дребезгом, пропуском импульса или ошибкой считывания. Поэтому алгоритм не должен реагировать на любое изменение входов как на реальный шаг. Он должен учитывать только те изменения, которые соответствуют допустимой последовательности состояний.

Период опроса влияет на максимальную скорость вращения, которую может корректно обработать программа. Если энкодер вращается быстрее, чем программа успевает считывать изменения, часть переходов будет пропущена. В результате может возникнуть ошибка подсчета шагов или неправильное определение направления. Поэтому при программном опросе необходимо выбирать период считывания с запасом относительно максимальной частоты сигналов энкодера. Пример ПО для взаимодействия с энкодером приведен в приложении А.

## 3.4 Дребезг и фильтрация сигналов энкодера

Механические контакты энкодера, как и контакты кнопок, подвержены дребезгу. Однако в случае энкодера дребезг влияет не на один сигнал, а на последовательность переходов двух каналов. Из-за этого возможны ложные шаги, изменение направления на один отсчет или появление некорректных состояний.

Особенность фильтрации энкодера состоит в необходимости сохранить быстрые полезные импульсы. Если применить слишком сильную фильтрацию, программа может потерять часть переходов при быстром вращении. Если фильтрация будет недостаточной, дребезг может быть принят за реальные изменения положения. Поэтому параметры фильтрации для энкодера должны выбираться с учетом максимальной скорости вращения и фактической длительности дребезга контактов.

Аппаратная фильтрация может выполняться с помощью RC-цепей или входов с триггером Шмитта. Такой подход сглаживает быстрые колебания до поступления сигнала на микроконтроллер, но добавляет элементы в схему и может ограничить максимальную частоту сигналов. В выбранном модуле KY-040 аппаратная фильтрация уже предусмотрена на плате модуля.

Для многофункционального вывода MIK32 в цифровом режиме технические условия задают входное напряжение низкого уровня UIL в диапазоне от 0 до 0,35*Ucc, а входное напряжение высокого уровня UIH - в диапазоне от 0,65*Ucc до Ucc [22, табл. 3]. При номинальном питании Ucc = 3,3 В это соответствует напряжению до 1,16 В для гарантированного логического нуля и от 2,15 В для гарантированной логической единицы. Поэтому под уровнем логической единицы в данном случае понимается достижение входного порога UIH микроконтроллера, то есть минимального входного напряжения, которое гарантированно воспринимается как логическая «1».

Для лабораторного макета важно не только получить работоспособный алгоритм, но и показать влияние фильтрации на результат. Поэтому при экспериментальной проверке необходимо измерить сигналы каналов энкодера, оценить максимальную частоту при быстром вращении и проверить, не приводит ли выбранный фильтр к потере полезных импульсов. Для оценки предельного режима энкодер вращался между двумя ладонями: такой способ позволяет получить скорость выше обычного поворота ручки пальцами и проверить, при какой скорости фронты после RC-фильтра становятся слишком растянутыми, а отдельные переходы начинают теряться. Осциллограмма приведена на рисунке 3.2.

При проверке RC-фильтра модуля было установлено, что он справляется с подавлением дребезга при ручном вращении энкодера. Время перехода сигнала от уровня логического нуля до уровня логической единицы составило около 2 мс.

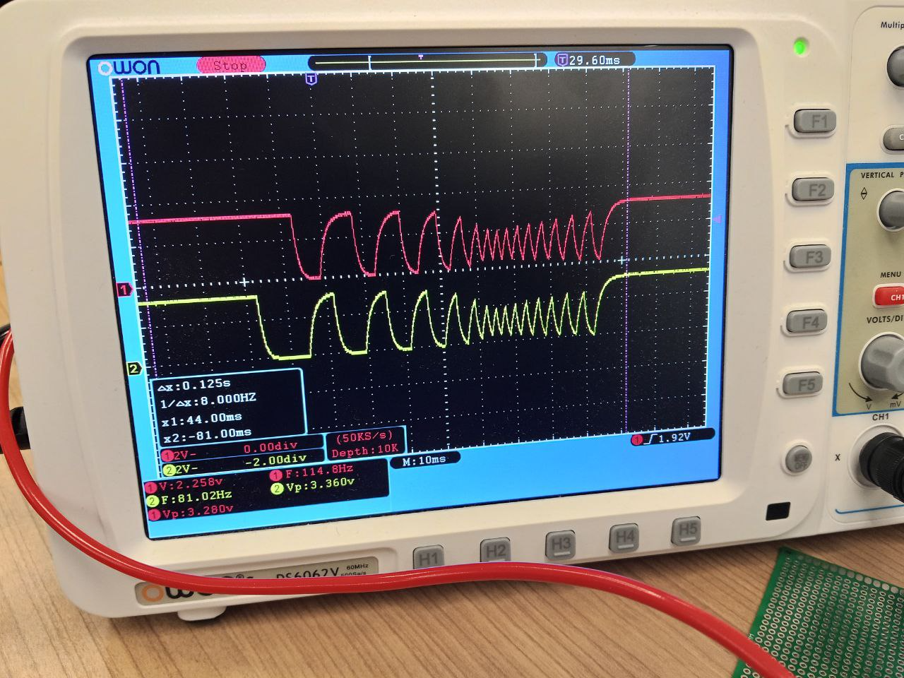
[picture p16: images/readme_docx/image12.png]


###### Рисунок 3.2 — Осциллограмма сигналов энкодера при быстром вращении

Проведенные тесты показали, что аппаратная фильтрация модуля KY-040 достаточна для работы макета: при полном обороте примерно за 500 мс программа не теряла состояния и корректно определяла направление вращения. Такая скорость выше обычного вращения пальцами, поэтому для лабораторного макета выбранная фильтрация и период опроса являются достаточными.

## 3.5 Подключение аналоговых ручек вращения

Аналоговые устройства ввода применяются для задания плавно изменяющихся параметров. Наиболее простой вариант такого устройства - потенциометр. В выбранной реализации применен Bourns PTV09A-4225F-B103, 10 кОм [23]. Нижний крайний вывод потенциометра подключается к земле, верхний крайний вывод получает питание от линии 3,3 В через резистор 20 кОм, а средний вывод подключается непосредственно к аналоговому входу микроконтроллера. Левый потенциометр подключается к первому каналу АЦП, правый - ко второму.

При подключении потенциометра необходимо согласовать диапазон напряжений с допустимым диапазоном входа АЦП. Для MIK32 АМУР диапазон входного сигнала АЦП составляет от 0,015 до UREF, где UREF находится в пределах от 1,1 до 1,3 В и имеет номинальное значение 1,2 В [1]. Поскольку сопротивление потенциометра составляет 10 кОм, резистор 20 кОм между питанием 3,3 В и верхним выводом потенциометра образует делитель напряжения. В результате напряжение на верхнем выводе потенциометра составляет около 1,1 В, а напряжение на среднем выводе изменяется в диапазоне примерно от 0 до 1,1 В в зависимости от положения ручки. Схема подключения представлена на рисунке 3.3.

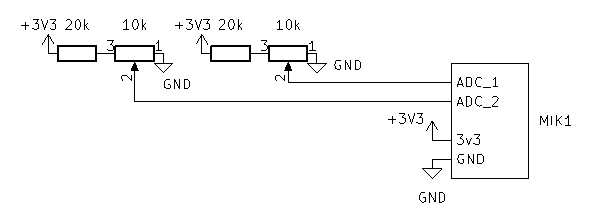
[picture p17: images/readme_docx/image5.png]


###### Рисунок 3.3 — Схема подключения потенциометров

## 3.6 Программная обработка аналоговых значений

MIK32 АМУР содержит один многоканальный АЦП, к входу которого сигналы подключаются через внутренний аналоговый коммутатор [24]. Поэтому при работе с двумя потенциометрами программа не измеряет оба канала одновременно, а последовательно выбирает нужный канал и запускает преобразование.

При переключении каналов необходимо учитывать задержку коммутации. В статье с экспериментальной проверкой АЦП MIK32 отмечается, что после выбора нового канала полезно выполнить холостое преобразование, так как первое измерение после переключения может относиться к переходному процессу [24]. Этот подход использован в программе: после выбора канала выполняется первое одиночное преобразование, его результат отбрасывается, затем выполняется второе преобразование, и только оно используется как текущее значение потенциометра.

Для проверки работы потенциометров был подготовлен простой пример. В нем настраивается АЦП MIK32 и периодически опрашиваются два аналоговых канала: канал 1 для левой ручки и канал 2 для правой ручки. Полученное значение АЦП является безразмерным кодом. В примере оно переводится в милливольты по опорному напряжению АЦП и дополнительно масштабируется в проценты от полного диапазона. Такой вывод удобен при отладке: сырое значение позволяет видеть фактический код АЦП, значение в милливольтах - проверить соответствие электрической схеме, а проценты - оценить положение ручки в форме, удобной для прикладной программы.

Даже при неподвижной ручке результат АЦП может немного изменяться из-за шумов и внутренних особенностей преобразователя. В статье также отмечаются дрейф и разброс показаний при длительном измерении постоянного напряжения [24]. Для лабораторного макета это не является критичным, так как потенциометры используются как органы плавного задания параметра, а не как точный измерительный прибор. В примере из приложения А применяется экспоненциальное сглаживание - один из наиболее простых алгоритмов сглаживания последовательности измерений [25]. Новое измерение вносит одну восьмую результата, а семь восьмых сохраняются от предыдущего значения. Такая фильтрация уменьшает мелкие колебания показаний и сохраняет достаточно быструю реакцию на поворот ручки.

# 4 Монтаж и отладка платы пользовательского ввода

Данный раздел посвящен практической реализации разработанных схемотехнических и программных решений. Рассматриваются монтаж платы пользовательского ввода, разработка библиотеки для работы с устройствами ввода, экспериментальная проверка работоспособности отдельных узлов и возможность применения платы в составе лабораторного макета.

## 4.1 Монтаж платы пользовательского ввода

На текущем этапе плата пользовательского ввода выполнена как самостоятельный модуль размером примерно 7x9 см и подключается к отладочной плате с микроконтроллером проводами-перемычками. Все органы управления установлены на одной плате и припаяны, поэтому при выполнении лабораторных работ не требуется каждый раз собирать кнопки, переключатели, энкодер и потенциометры на макетной плате. Это уменьшает время подготовки, повышает повторяемость экспериментов и снижает вероятность ошибок подключения. Внешний вид получившейся платы представлен на рисунке 4.1.

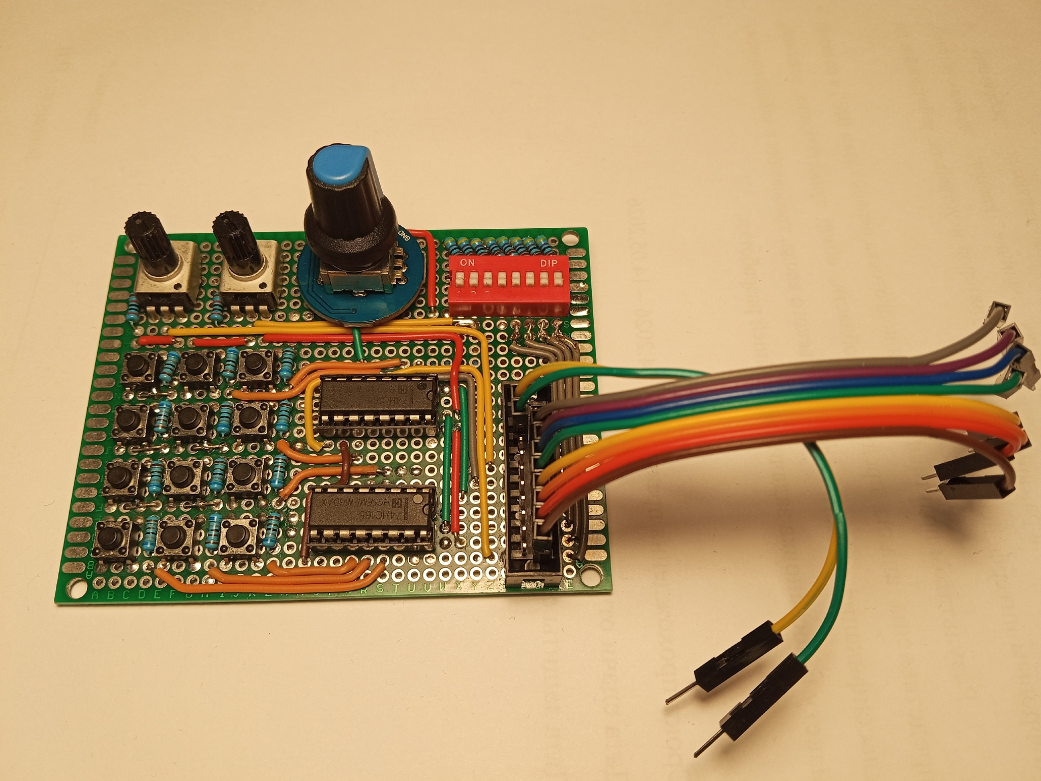
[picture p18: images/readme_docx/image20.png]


###### Рисунок 4.1 — Внешний вид платы пользовательского ввода

Полная электрическая схема платы пользовательского ввода приведена на рисунке 4.2

.

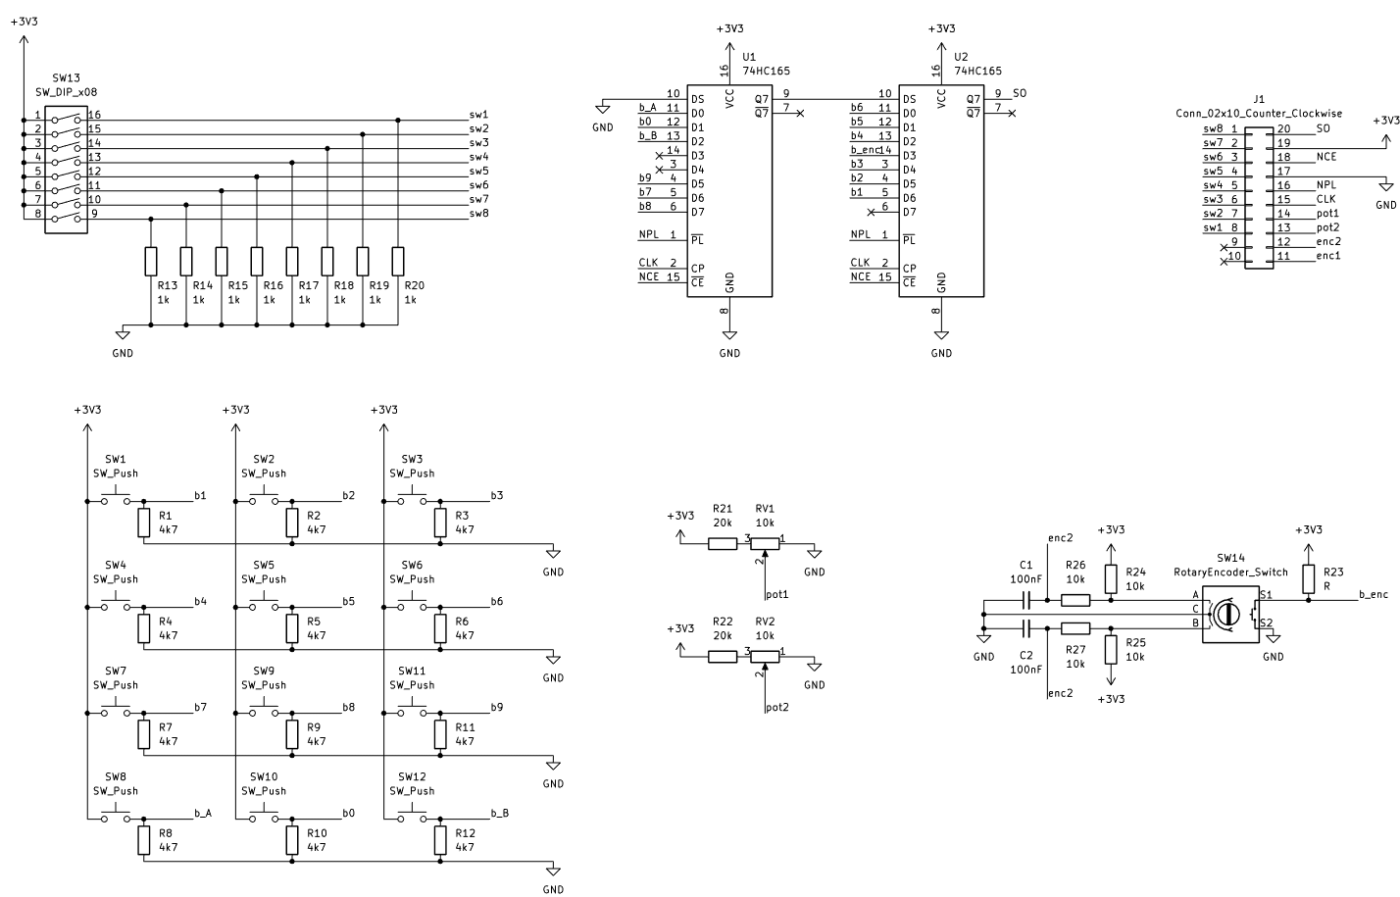
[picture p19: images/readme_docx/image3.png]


###### Рисунок 4.2 — Схема платы пользовательского ввода

В дальнейшем модуль пользовательского ввода будет перенесен на единую лабораторную плату и объединен с устройствами вывода, индикацией, цепями питания, разъемами расширения и другими узлами учебного стенда.

Для подключения модуля к отладочной плате используется распределение выводов, приведенное в таблице 4.1. В нем выбраны такие линии микроконтроллера, при которых кнопки, переключатели, энкодер и аналоговые ручки работают независимо и не используют одни и те же входы. В библиотеке, которая будет рассмотрена в следующем подразделе программно заданы именно эти входы/выходы МК.

Таблица 4.1 — Сопоставление входов/выходов MIK32 и разработанной платы

| Номер выхода на плате пользовательского ввода. | Вход/выход MIK32 |
| --- | --- |
| 1 | P1.8 |
| 2 | P1.9 |
| 3 | P1.1 |
| 4 | P1.4 |
| 5 | P2.6 |
| 6 | P2.7 |
| 7 | P1.3 |
| 8 | P1.6 |
| 11 | P0.8 (Timer16_1_in1) |
| 12 | P0.9 (Timer16_1_in2) |
| 13 | P1.7 (ADC_1) |
| 14 | P0.2 (ADC_2) |
| 15 | P1.2 (SPI1_clk) |
| 16 | P1.5 (SPI1_n_ss_out_1) |
| 17 | Gnd |
| 18 | Gnd |
| 19 | Vcc |
| 20 | P1.0 (SPI1_MISO) |

## 4.2 Библиотека для работы с устройствами ввода

Для упрощения использования платы была разработана библиотека lab_input.h (Приложение Б). Она скрывает низкоуровневую настройку периферии и предоставляет простой программный интерфейс для учебных и проектных работ, включая лабораторные, курсовые, выпускные квалификационные и самостоятельные разработки. Инициализация выполняется функцией li_init(), а регулярный опрос устройств - функцией li_update(), которую необходимо вызывать с периодом 1 мс. Внутри библиотеки выполняется опрос энкодера, чтение кнопок через сдвиговые регистры 74HC165 по SPI, считывание аналоговых ручек через АЦП и хранение текущих состояний.

Библиотека предоставляет функции получения состояний устройств ввода: li_get_keyboard_bitmask() для кнопочной клавиатуры, li_get_button_state() для отдельной кнопки, li_get_levers_bitmask() для рычажковых переключателей, li_get_enc_counter() для счетчика энкодера и li_get_pot_value_mv() для значений потенциометров в милливольтах. Благодаря этому в учебных программах можно использовать готовые органы управления без повторной настройки GPIO, SPI и АЦП. Пример использования всех возможностей библиотеки находится в приложении А.

Такой подход особенно полезен для работ, которые направлены не на изучение самих устройств ввода, а на другие темы: обработка данных с внешних датчиков, взаимодействие с устройствами вывода и так далее. В этих случаях кнопки, переключатели, энкодер и потенциометры нужны как источник команд и параметров, а библиотека позволяет подключить их к программе с минимальным количеством служебного кода.

## 4.3 Тестирование и экспериментальная проверка

Разработанная плата и библиотека были проверены в различных пользовательских сценариях.

Был проведен тест многократного нажатия всех кнопок и смены состояния переключателей. Программой было верно определено количество нажатий.

Поворотный энкодер проверялся при обычном ручном вращении, при полном обороте примерно за 500 мс и в предельном режиме вращения между двумя ладонями. Эти испытания позволили оценить корректность определения направления и влияние аппаратной фильтрации на форму сигналов. Потенциометры проверялись через АЦП: программа считывала оба канала, масштабировала значения в милливольты и позволяла наблюдать изменение результата при повороте ручек. Стоит обратить внимание, что передача состояний всех устройств через UART нарушает частоту вызова функции li_update(), из-за этого в примере из приложения А, энкодер может пропускать шаги.

В результате проверки подтверждено, что все устройства ввода опрашиваются и работают в типовых сценариях использования: нажатие отдельных и нескольких кнопок, изменение положения переключателей, вращение энкодера в обе стороны и плавное изменение положения аналоговых ручек. Это подтверждает пригодность разработанной платы для использования в составе лабораторного макета MIK32 АМУР.

## 4.4 Плата пользовательского ввода как часть лабораторного макета

Следующим этапом развития лабораторного макета должна стать разработка объединенной платы, которая совместит в себе устройства пользовательского ввода, устройства вывода и систему питания. Такая плата позволит избежать использования десятков проводов-перемычек между отдельными платами и значительно упростит выполнение ЛР.

При проектировании объединенной платы рекомендуется сохранить возможность ручной коммутации сигналов. Для этого на всех входах и выходах пользовательского ввода следует предусмотреть перемычки-мосты. Они позволят отключать отдельные органы управления от микроконтроллера, менять назначение линий, подключать внешние устройства и проводить лабораторные работы, в которых требуется самостоятельно выбирать способ соединения узлов макета. Наличие перемычек также упрощает поиск неисправностей, поскольку каждую функциональную часть можно временно изолировать от остальных цепей.

Для удобства измерений на каждой сигнальной линии рекомендуется установить отдельный штыревой контакт формата DIP. Такие контрольные точки позволяют быстро подключать щуп осциллографа или логического анализатора к линиям кнопок, переключателей, клавиатуры, энкодера, сдвиговых регистров, аналоговых входов и устройств вывода. Контрольные контакты следует располагать рядом с соответствующими перемычками и подписывать на шелкографии теми же обозначениями, которые используются на электрической схеме.

Возможное расположение компонентов объединенной платы и рекомендуемая схема шелкографии приведены на рисунке 4.3.

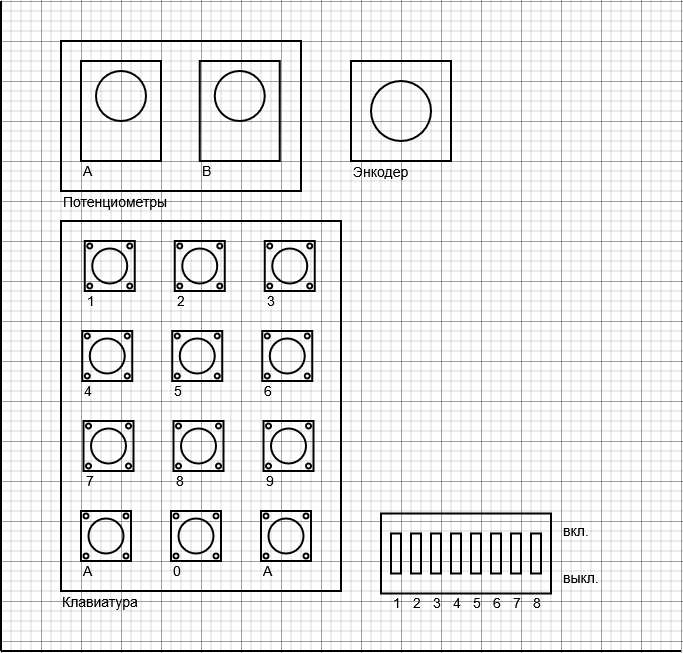
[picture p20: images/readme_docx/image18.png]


###### Рисунок 4.3 - Возможное расположение компонентов и рекомендуемая схема шелкографии объединенной лабораторной платы

# 5 Безопасность жизнедеятельности

Данный раздел посвящен анализу условий применения платы пользовательского ввода и оценке факторов, которые могут влиять на безопасность при разработке, отладке и эксплуатации макета. Рассматриваются возможные опасные и вредные факторы, а также мероприятия, направленные на снижение риска при работе с лабораторным оборудованием.

## 5.1 Общая характеристика условий применения

Выпускная квалификационная работа посвящена разработке платы пользовательского ввода для лабораторного макета на базе микроконтроллера MIK32 АМУР. Разрабатываемый модуль предназначен для применения в учебной лаборатории при выполнении лабораторных и самостоятельных работ.

Основными пользователями макета являются студенты, работающие с платой под руководством преподавателя. Разработанная плата используется не как промышленное изделие, а как учебное техническое средство. Жизненный цикл разработки включает несколько этапов: анализ требований, проектирование электрической схемы, разработку программного обеспечения, монтаж опытного образца, пайку компонентов, экспериментальную проверку, эксплуатацию в учебной лаборатории, хранение и возможную доработку платы. На этапе проектирования и программирования основная работа выполняется за персональным компьютером с использованием системы автоматизированного проектирования, среды разработки, текстового редактора и технической документации. На этапах изготовления и отладки применяются паяльное оборудование, лабораторные источники питания, отладочная плата с микроконтроллером, мультиметр и осциллограф.

Разрабатываемая плата относится к низковольтным электронным устройствам. Основные рабочие напряжения сигнальных цепей составляют 3,3 В, а аналоговые сигналы, поступающие на входы АЦП, дополнительно ограничиваются до диапазона, допустимого для микроконтроллера. При штатной эксплуатации такие уровни напряжения не представляют самостоятельной опасности поражения электрическим током. Однако плата используется совместно с сетевым оборудованием: персональным компьютером, блоком питания, осциллографом, паяльной станцией и другой лабораторной аппаратурой. Поэтому требования безопасности должны рассматриваться не только для самой платы, но и для всей системы «пользователь — лабораторное оборудование — макет — программное обеспечение».

Особенностью учебного применения является то, что с макетом работают пользователи с разным уровнем подготовки. Студенты могут ошибиться при подключении питания, перепутать линии VCC и GND, подать на вход микроконтроллера недопустимый уровень напряжения, случайно замкнуть соседние контакты щупом осциллографа или неправильно использовать программный пример. Такие ситуации, как правило, не создают прямой угрозы жизни из-за низких рабочих напряжений платы, но могут привести к нагреву элементов, повреждению микроконтроллера, отказу лабораторного оборудования и нарушению учебного процесса. Следовательно, при разработке необходимо обеспечить допустимый уровень риска за счет схемотехнических, программных и организационных мер.

## 5.2 Идентификация опасных и вредных факторов

Идентификация опасных и вредных факторов выполняется с учетом классификации, приведенной в ГОСТ 12.0.003–2015 [26]. Для данной разработки наиболее значимыми являются физические, химические и психофизиологические факторы. Биологические факторы для рассматриваемого макета не являются существенными, так как работа не связана с биологическими материалами, микроорганизмами или источниками биологического воздействия.

К физическим факторам относятся опасность поражения электрическим током при использовании сетевого оборудования, возможность короткого замыкания в низковольтных цепях, нагрев элементов при ошибочном подключении, воздействие высокой температуры при пайке, недостаточная освещенность рабочего места, электромагнитные помехи и вероятность механического повреждения элементов платы. Несмотря на то что сама плата работает с напряжением 3,3 В, лабораторный комплекс включает устройства, подключаемые к сети 220 В. Поэтому неисправность блока питания, паяльной станции, компьютера или измерительного прибора может привести к появлению опасного напряжения на доступных частях оборудования.

Отдельный риск связан с ошибками коммутации. На этапе отладки плата подключается к отладочной плате проводами-перемычками. При большом количестве сигнальных линий возможно неверное соединение контактов, подача питания обратной полярности, замыкание питания на землю, соединение выхода одного устройства с выходом другого устройства или подача на вход MIK32 сигнала с недопустимым уровнем. Для цифровых входов микроконтроллера допустимыми являются уровни, согласованные с питанием 3,3 В; подача уровня 5 В на входы не допускается. Для аналоговых входов опасность отказа дополнительно связана с превышением допустимого диапазона АЦП. Поэтому в схеме потенциометров используется делитель напряжения, ограничивающий максимальное напряжение на входе микроконтроллера примерно до 1,1 В.

При монтаже платы появляется фактор повышенной температуры. Жало паяльника и нагретые выводы компонентов могут вызвать ожог. Кроме того, при пайке выделяются дым и пары флюса, которые относятся к химическим факторам и могут раздражать органы дыхания. В штатной учебной эксплуатации платы химические факторы практически отсутствуют, однако на этапе изготовления и ремонта они должны учитываться.

Пожарная опасность для разрабатываемого макета невелика из-за низкой мощности устройства, но полностью не исключается. Короткое замыкание, длительная перегрузка источника питания, использование неисправного кабеля или оставленная без присмотра паяльная станция могут привести к локальному нагреву, оплавлению изоляции или повреждению печатной платы. Поэтому вопросы пожарной безопасности должны рассматриваться совместно с требованиями к электробезопасности и организации рабочего места.

Психофизиологические факторы связаны с характером труда разработчика и пользователя макета. При проектировании схемы, написании программы и отладке кода работа выполняется преимущественно сидя, с длительным зрительным напряжением и статической нагрузкой на мышцы спины, шеи, плечевого пояса и кистей. При работе с документацией, исходным кодом, осциллограммами и мелкими элементами платы возникает перенапряжение зрительного анализатора. Нервно-эмоциональная нагрузка может проявляться при поиске труднообнаруживаемых ошибок во время выполнения ЛР.

Особое внимание следует уделить программному обеспечению. В работе разработана библиотека lab_input.h, предназначенная для опроса устройств ввода и предоставления пользователю простого программного интерфейса. Ошибки в программной части не создают прямой опасности для человека, поскольку библиотека не управляет силовыми исполнительными механизмами. Однако неправильная настройка GPIO, нарушение периода вызова функции опроса, ошибочная обработка энкодера, отсутствие подавления дребезга или неверное масштабирование значений АЦП могут привести к ложной интерпретации действий пользователя, неверным результатам лабораторной работы и, в отдельных случаях, к конфликту сигналов на выводах микроконтроллера.
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

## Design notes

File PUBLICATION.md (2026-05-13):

# Разработка средств пользовательского ввода для лабораторного макета микроконтроллера MIK32 АМУР

## Введение

Использование в учебном процессе лабораторного макета микроконтроллера позволяет исключить сборку схем на макетной плате и обеспечить повторяемость выполнения лабораторных работ. Макет позволяет студентам быстрее перейти к программированию и проверке работы периферийных модулей. Учебный макет должен включать органы управления, устройства индикации, разъемы расширения, внешние интерфейсы и цепи питания. Для популярных зарубежных платформ доступно много готовых учебных наборов и дополнительных модулей. Для микроконтроллера MIK32 АМУР существуют отладочные платы и модули, например DIP-MIK32, СТАРТ-MIK32 и RADIANT MIK32, однако с точки зрения пользовательского ввода такие платы обычно ограничены одной-двумя кнопками и несколькими светодиодами[3,4,5], поэтому аппаратные узлы учебного стенда приходится разрабатывать отдельно.

В этой публикации рассматривается не весь лабораторный макет, а одна его часть - плата пользовательского ввода. Она объединяет устройства, с помощью которых пользователь формирует входные сигналы: кнопки, переключатели, клавиатуру, поворотный энкодер и потенциометры. На этих элементах можно отработать настройку портов ввода-вывода, обработку дребезга контактов, опрос клавиатуры, применение сдвиговых регистров, работу таймеров, прерываний, аналого-цифрового преобразователя и цифровых интерфейсов SPI, USART и I2C.

Для выполнения лабораторных работ с несколькими кнопками, переключателями, энкодером или аналоговыми регуляторами приходится собирать дополнительные схемы на макетной плате. Это увеличивает время подготовки, повышает вероятность ошибок подключения и затрудняет повторяемость экспериментов в учебной аудитории.

На текущем этапе плата пользовательского ввода выполнена как самостоятельный модуль и подключается к отладочной плате с микроконтроллером проводами-перемычками. В дальнейшем эти решения планируется перенести на общую лабораторную плату, где пользовательский ввод будет объединен с устройствами вывода, индикацией, разъемами расширения и другими узлами учебного стенда.

Цель публикации - обосновать необходимость разработки отдельной платы пользовательского ввода для учебного макета на базе микроконтроллера MIK32 АМУР и описать основные аппаратные и программные решения, применяемые при ее создании.

### 1. Назначение и состав модуля пользовательского ввода

Лабораторный макет должен обеспечивать работу с основными типами входных сигналов: дискретными, аналоговыми, импульсными и сигналами, передаваемыми через цифровые интерфейсы. Для учебных целей достаточно включить в макет один или несколько характерных элементов каждого типа: после освоения базового принципа считывания и фильтрации его можно перенести на другие устройства того же класса.

Дискретный ввод представлен тактовыми кнопками и рычажковыми переключателями. К этому типу также относятся концевые выключатели, герконы, датчики открытия и датчики с релейным выходом. Кнопки подходят для изучения кратковременных событий нажатия и отпускания, а переключатели - для задания устойчивых логических состояний. На этих элементах удобно рассматривать настройку GPIO, подтягивающие резисторы и обработку дребезга контактов. В модуле используется набор из 8 DIP-переключателей, а также клавиатура из 12 кнопок, подключаемых через сдвиговые регистры 74HC165. Такой способ подключения уменьшает число занятых выводов микроконтроллера и позволяет отработать передачу состояний внешних устройств через цифровой интерфейс.

Аналоговый ввод реализован на потенциометрах. По принципу обработки к ним близки аналоговые джойстики, фоторезисторы, терморезисторы и датчики положения. Потенциометр удобен как простой источник регулируемого напряжения: на его примере можно изучить работу АЦП и фильтрацию шумов.

Импульсный ввод реализован на поворотном энкодере. К этому типу также относятся датчики скорости вращения, тахометрические датчики, оптические прерыватели и датчики положения с импульсным выходом. Энкодер позволяет изучить обработку двух связанных каналов, определение направления вращения и влияние частоты опроса.

### 2. Рычажковые переключатели

Рычажковые переключатели применяются для задания устойчивых логических состояний, например выбора режима работы программы или имитации простых дискретных датчиков. В модуле предусмотрено 8 DIP-переключателей, подключенных к входам GPIO микроконтроллера. Для исключения неопределенного состояния входов используются подтягивающие резисторы.

Экспериментально определены частота переключения и длительность дребезга контактов. Максимальная частота переключения рычажков составила около 3 Гц. Длительность дребезга рычажковых переключателей не превысила 7 мс. Длительность дребезга использованных кнопок не превышала 2 мс, а минимальная длительность уверенного нажатия при проверке составила около 40 мс. Пример временной диаграммы нажатия кнопки и изменения состояния переключателя приведен на рис. 1.

Временная диаграмма нажатия кнопки и смены состояния переключателя

_Рис. 1. Временная диаграмма нажатия кнопки._

Для подавления дребезга рассмотрены три варианта. Первый - специализированная микросхема MC14490 для аппаратной обработки механических контактов. [1,2] Второй - RC-фильтр нижних частот на резисторе и конденсаторе, сглаживающий короткие импульсы перед подачей сигнала на вход микроконтроллера. [1] Эти аппаратные варианты показаны на рис. 2. Третий вариант - программная фильтрация, при которой новое состояние принимается только после сохранения в течение заданного времени. [1] Проверка подтвердила работоспособность всех трех вариантов.

Схемы аппаратного подавления дребезга контактов

_Рис. 2. Схемы аппаратного подавления дребезга контактов._

Сравнение способов подавления дребезга для блока из 8 переключателей приведено в табл. 1.

_Таблица 1. Сравнение способов подавления дребезга контактов._

| Способ | Примерная цена | Доступность | Сложность монтажа | Сложность программирования |
| --- | --- | --- | --- | --- |
| MC14490 | ~300 руб. | низкая, срок доставки около 6 недель | средняя | низкая |
| RC-фильтр | ~500 руб. | высокая | высокая | низкая |
| Программная фильтрация | - | - | низкая | средняя |

Для макета выбрана программная фильтрация дребезга. Рычажковые переключатели опрашиваются с периодом 30 мс. Переключение фиксируется только в том случае, если новое состояние сохраняется при следующем опросе.

### 3. Кнопочная клавиатура

Кнопочная клавиатура предназначена для изучения кратковременных дискретных событий: нажатия, отпускания и удержания кнопки. В модуле используются 12 тактовых кнопок, подключенных через два сдвиговых регистра 74HC165. Один регистр имеет 8 параллельных входов и передает их состояния последовательно, поэтому две микросхемы позволяют считать все кнопки при малом числе занятых выводов MIK32.

Для клавиатуры сравнивались три варианта подключения: напрямую к GPIO, матрицей 4x3 и через сдвиговые регистры 74HC165. Выбран вариант со сдвиговыми регистрами, так как он занимает меньше выводов и дает возможность отработать обмен по аппаратному SPI. Регистры объединены в цепочку, а выход последнего регистра подключается к линии MISO через резистор 1 кОм, чтобы уменьшить риск конфликта на общей SPI-шине.

Готовых примеров работы с 74HC165 для MIK32 найти не удалось, поэтому для макета написан собственный драйвер. Он формирует сигнал загрузки состояний кнопок, считывает данные по SPI и преобразует полученное значение в битовую маску. Затем программа использует эту маску для определения нажатий и фильтрации дребезга: состояние кнопки принимается только при сохранении в течение 10 мс.

При работе с SPI на MIK32 были обнаружены две особенности. Сигнал CS инвертирован, поэтому им приходится управлять вручную. Кроме того, линия CLK после завершения обмена не сразу возвращается к нулю и устанавливается в низкий уровень только через несколько миллисекунд, но это не нарушает целостности сообщения.

### 4. Поворотный энкодер

Поворотный энкодер используется для изучения импульсных входных сигналов. Он формирует две последовательности импульсов на каналах A и B, по которым программа определяет направление вращения и изменение положения. В текущей версии макета используется готовый модуль энкодера, уже содержащий RC-фильтр для подавления дребезга. В дальнейшем эту часть схемы можно перенести непосредственно на общую лабораторную плату, но на этапе разработки модуль установлен целиком.

Работа энкодера проверена экспериментально. При полном обороте за 500 мс программа не теряла состояния и корректно определяла направление вращения. Такой скорости достаточно для ручного управления, поскольку в обычном режиме пользователь вращает энкодер медленнее, чем в предельном тесте.

Готовый драйвер энкодера для MIK32 также найти не удалось, поэтому обработка входного сигнала реализована самостоятельно.

### 5. Потенциометры

Потенциометры используются как источник аналогового сигнала и позволяют вручную задавать плавно изменяющееся напряжение. В модуле установлены два потенциометра номиналом 10 кОм, подключенные к входам АЦП микроконтроллера. Для ограничения напряжения на выходе при питании 3,3 В в цепь каждого канала добавлен резистор 20 кОм, потому что максимальное напряжение на входе АЦП составляет около 1,1 В [6].

Программа считывает результаты преобразования, масштабирует их в удобный диапазон и при необходимости фильтрует небольшие шумовые колебания. На этом примере можно изучить работу АЦП и обработку аналоговых данных.

### Заключение

В публикации рассмотрена разработка отдельной платы пользовательского ввода для лабораторного макета на базе отечественного микроконтроллера MIK32 АМУР. Плата подключается к отладочной плате проводами-перемычками; ее внешний вид показан на рис. 3. В дальнейшем схемные решения платы планируется перенести на общую печатную плату.

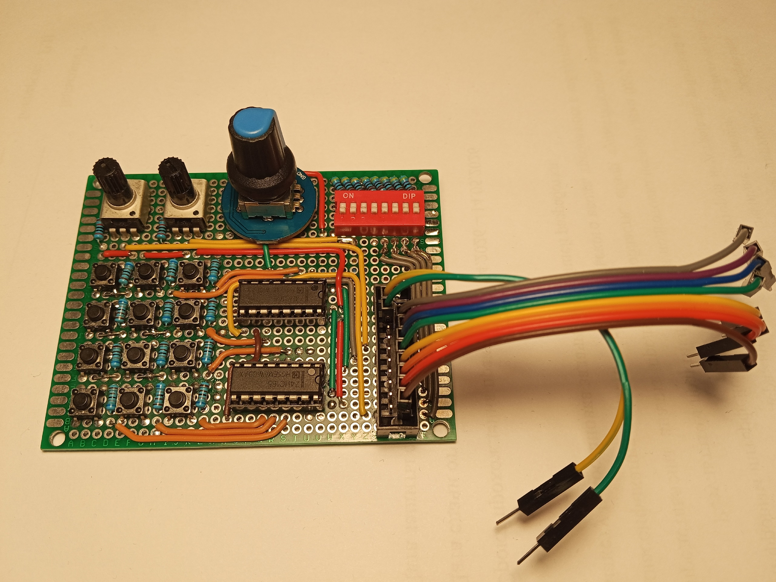
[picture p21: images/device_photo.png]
Внешний вид платы пользовательского ввода


_Рис. 3. Внешний вид платы пользовательского ввода._

В состав платы вошли рычажковые переключатели, кнопочная клавиатура на сдвиговых регистрах 74HC165, поворотный энкодер и два потенциометра. Эти устройства позволяют изучать дискретный, импульсный и аналоговый ввод, а также работу с внешними цифровыми микросхемами по SPI.

Для переключателей и кнопок проведены измерения частоты срабатываний и длительности дребезга. После сравнения аппаратных и программных способов подавления дребезга для макета выбрана программная фильтрация. Для клавиатуры и энкодера написаны собственные драйверы под MIK32, так как готовых примеров для этой платформы найти не удалось.

Экспериментальная проверка показала работоспособность выбранных решений. В дальнейшем разработанные узлы могут быть перенесены на единую лабораторную плату, объединяющую пользовательский ввод, средства вывода, индикацию и дополнительные интерфейсы. Полная электрическая схема платы приведена на рис. 4.

Схема платы пользовательского ввода

_Рис. 4. Схема платы пользовательского ввода._

### Список источников

1. Ganssle J. A Guide to Debouncing. URL: https://my.eng.utah.edu/~cs5780/debouncing.pdf

2. Onsemi. MC14490 Hex Contact Bounce Eliminator. URL: https://www.mouser.com/datasheet/2/308/MC14490-D-77744.pdf

3. АО «Микрон». DIP-MIK32: руководство пользователя. URL: https://docs.mikron.ru/wiki/_attachments/DIP-MIK32-V4-MANUAL-R1.4.pdf

4. Tellur Electronics. Старт-MIK32. URL: https://tellur-el.ru/catalog/razrabotka_i_konstruirovanie_1/otladochnye_platy_1/328685/

5. Tellur Electronics. RADIANT MIK32: руководство пользователя. URL: https://tellur-el.ru/upload/iblock/683/vf01f8cuoblf7f9xdsvoab582c1hciqu/797126be_fe7e_11ef_b2d6_000c29da4576_3ddd7085_219b_11f0_aed8_0050568bb3a7.pdf

6. АО «Микрон». Информационный лист MIK32 АМУР. URL: https://docs.mikron.ru/wiki/_attachments/Information_AMUR_MIK32_r1_2.pdf

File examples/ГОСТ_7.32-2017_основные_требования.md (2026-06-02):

# ГОСТ 7.32-2017: основные требования к оформлению

Краткий конспект по ГОСТ 7.32-2017 «СИБИД. Отчет о научно-исследовательской работе. Структура и правила оформления». Для ВКР СПбГЭТУ «ЛЭТИ» требования ГОСТ следует применять вместе с методическими указаниями ЛЭТИ и кафедральным чек-листом нормоконтроля.

## Файл ГОСТ

Скачанная копия: `examples/ГОСТ_7.32-2017_скачано.pdf`

Также в проекте уже была локальная копия: `examples/ГОСТ 7.32-2017.pdf`

Источник скачивания: https://tsu.ru/upload/medialibrary/8cf/gost_7.32_2017.pdf

Официальная карточка Росстандарта: https://protect.gost.ru/gost/details/7d280e43-7036-4a69-8e6e-d15867028343

## Основные параметры страницы

| Параметр | Требование |
| --- | --- |
| Формат страницы | A4 |
| Печать | На одной стороне листа |
| Межстрочный интервал | 1,5 |
| Цвет шрифта | Черный |
| Размер шрифта | Не менее 12 пт |
| Рекомендуемый шрифт | Times New Roman |
| Левое поле | 30 мм |
| Правое поле | 15 мм |
| Верхнее поле | 20 мм |
| Нижнее поле | 20 мм |
| Абзацный отступ | 1,25 см, одинаковый по всему тексту |

Примечание: ГОСТ задает минимальный размер шрифта 12 пт. Для ВКР часто требуют 14 пт, поэтому итоговый размер лучше сверить с методичкой ЛЭТИ, шаблоном кафедры или чек-листом нормоконтроля.

## Шрифт и выделения

- Основной текст рекомендуется выполнять шрифтом Times New Roman.
- Полужирный шрифт применяют только для заголовков разделов, подразделов и структурных элементов.
- Курсив допускается для латинских терминов и специальных обозначений.
- Для акцентирования допускается начертание, отличное от основного, но того же кегля и гарнитуры.
- Качество текста, рисунков, таблиц и распечаток программ должно обеспечивать четкое воспроизведение.

## Нумерация страниц

- Страницы нумеруются арабскими цифрами сквозной нумерацией по всему тексту, включая приложения.
- Номер страницы ставится в центре нижней части страницы без точки.
- Титульный лист включается в общую нумерацию, но номер на нем не ставится.
- Иллюстрации и таблицы на отдельных листах включаются в общую нумерацию страниц.

## Структурные элементы

Заголовками структурных элементов служат:

- `СПИСОК ИСПОЛНИТЕЛЕЙ`
- `РЕФЕРАТ`
- `СОДЕРЖАНИЕ`
- `ТЕРМИНЫ И ОПРЕДЕЛЕНИЯ`
- `ПЕРЕЧЕНЬ СОКРАЩЕНИЙ И ОБОЗНАЧЕНИЙ`
- `ВВЕДЕНИЕ`
- `ЗАКЛЮЧЕНИЕ`
- `СПИСОК ИСПОЛЬЗОВАННЫХ ИСТОЧНИКОВ`
- `ПРИЛОЖЕНИЕ`

Правила:

- Заголовки структурных элементов располагаются по центру строки.
- Пишутся прописными буквами.
- Точка в конце не ставится.
- Подчеркивание не применяется.
- Каждый структурный элемент и каждый раздел основной части начинают с новой страницы.

## Разделы и подразделы

- Основная часть делится на разделы, подразделы и пункты.
- Разделы и подразделы должны иметь заголовки.
- Заголовки разделов и подразделов начинаются с абзацного отступа после номера.
- Заголовки печатаются с прописной буквы, полужирным шрифтом, без подчеркивания и без точки в конце.
- Переносы слов в заголовках не допускаются.
- Разделы нумеруются арабскими цифрами без точки в конце номера: `1`, `2`, `3`.
- Подразделы нумеруются в пределах раздела: `1.1`, `1.2`; точка в конце номера не ставится.
- Если раздел или подраздел состоит из одного пункта, пункт не нумеруется.

## Перечисления

- Перед элементами перечисления ставят тире.
- Если нужно сослаться на элемент перечисления, используют строчные буквы русского алфавита со скобкой: `а)`, `б)`, `в)`.
- Не используют буквы `ё`, `з`, `й`, `о`, `ч`, `ъ`, `ы`, `ь`.
- При конкретном числе элементов допускается использовать арабские цифры со скобкой: `1)`, `2)`, `3)`.
- Простые перечисления разделяются запятыми, сложные - точкой с запятой.
- Перечисления приводятся с абзацного отступа в столбик.

## Рисунки

- Иллюстрации размещают сразу после первого упоминания в тексте или на следующей странице.
- На все иллюстрации должны быть ссылки в тексте.
- При ссылке пишут слово `рисунок` и номер: например, `в соответствии с рисунком 2`.
- Иллюстрации нумеруются арабскими цифрами сквозной нумерацией: `Рисунок 1`, `Рисунок 2`.
- Допускается нумерация в пределах раздела: `Рисунок 2.1`.
- Подпись размещается под рисунком по центру.
- Формат подписи: `Рисунок 1 - Схема прибора`.
- Точка в конце подписи не ставится.
- Если название рисунка занимает несколько строк, его пишут через один межстрочный интервал.
- Перенос слов в названии рисунка не допускается.

## Таблицы

- Таблицу размещают сразу после первого упоминания в тексте или на следующей странице.
- На все таблицы должны быть ссылки в тексте.
- При ссылке пишут слово `таблица` и номер.
- Наименование таблицы размещают над таблицей слева без абзацного отступа.
- Формат подписи: `Таблица 1 - Наименование таблицы`.
- Точка в конце наименования таблицы не ставится.
- Если название таблицы занимает две строки и более, его пишут через один межстрочный интервал.
- Таблицы нумеруются арабскими цифрами сквозной нумерацией.
- Допускается нумерация в пределах раздела: `Таблица 2.3`.
- При переносе таблицы на следующую страницу над продолжением пишут: `Продолжение таблицы 1`.
- Заголовки граф и строк пишут с прописной буквы.
- В конце заголовков и подзаголовков таблиц точки не ставятся.
- В таблице допускается применять размер шрифта меньше, чем в основном тексте.

## Формулы

- Формулы и уравнения выделяют из текста в отдельную строку.
- Выше и ниже формулы оставляют не менее одной свободной строки.
- Формулы располагают посередине строки.
- Нумерация формул ставится арабскими цифрами в круглых скобках справа: `(1)`.
- Ссылки на формулы приводят в скобках: `в формуле (1)`.
- Пояснение символов приводят непосредственно под формулой.
- Первую строку пояснения начинают словом `где` без двоеточия.

## Список источников

- Источники располагают в порядке появления ссылок в тексте.
- Нумеруют арабскими цифрами с точкой.
- Печатают с абзацного отступа.

## Приложения

- На все приложения должны быть ссылки в тексте.
- Приложения располагают в порядке ссылок на них.
- Каждое приложение начинают с новой страницы.
- В центре верхней части страницы пишут слово `ПРИЛОЖЕНИЕ`.
- Приложение должно иметь заголовок: с прописной буквы, полужирным шрифтом, отдельной строкой по центру, без точки в конце.
- Приложения обозначают буквами русского алфавита, начиная с `А`, кроме `Ё`, `З`, `Й`, `О`, `Ч`, `Ъ`, `Ы`, `Ь`.
- Страницы приложений входят в общую сквозную нумерацию.

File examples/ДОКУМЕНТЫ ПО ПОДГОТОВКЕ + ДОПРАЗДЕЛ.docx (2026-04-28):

Для ознакомления с материалами для написания дополнительного раздела заходим вот сюда:

https://etu.ru/ru/studentam/dokumenty-dlya-ucheby/dlya-podgotovki-vkr

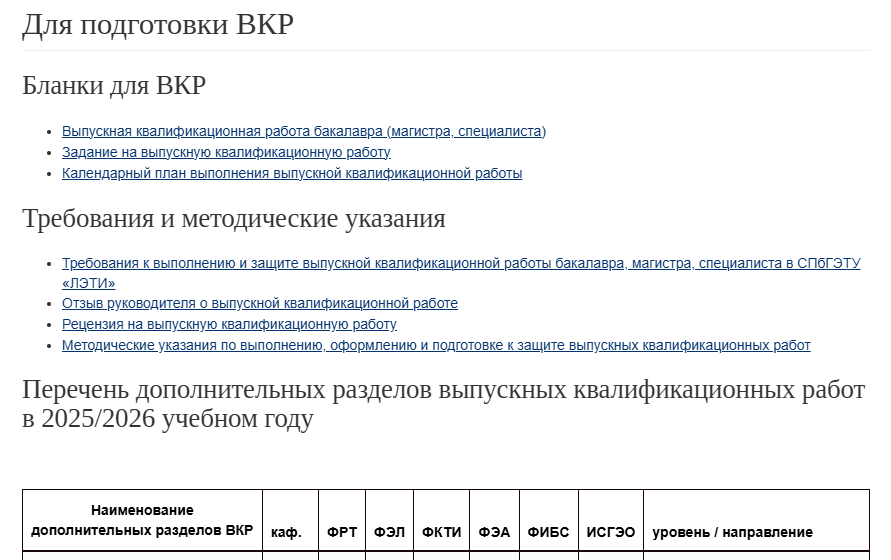
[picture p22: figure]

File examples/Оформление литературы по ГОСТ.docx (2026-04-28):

1. Заходим на Гугл.Академию https://scholar.google.com
2. Вбиваем название нужного источника и жмем кнопку «Цитировать»

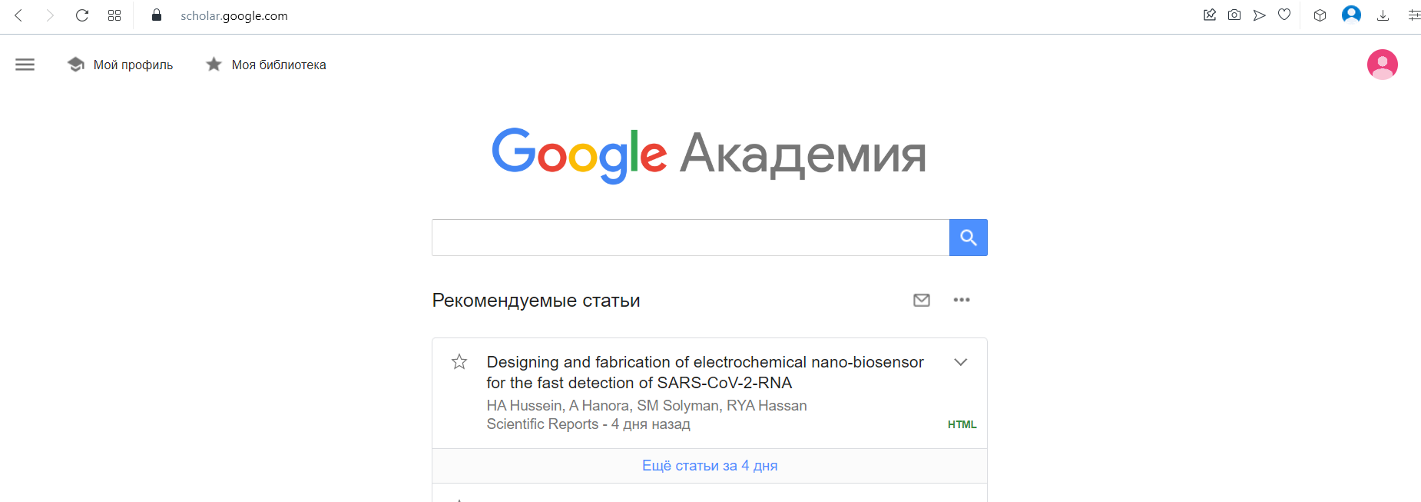
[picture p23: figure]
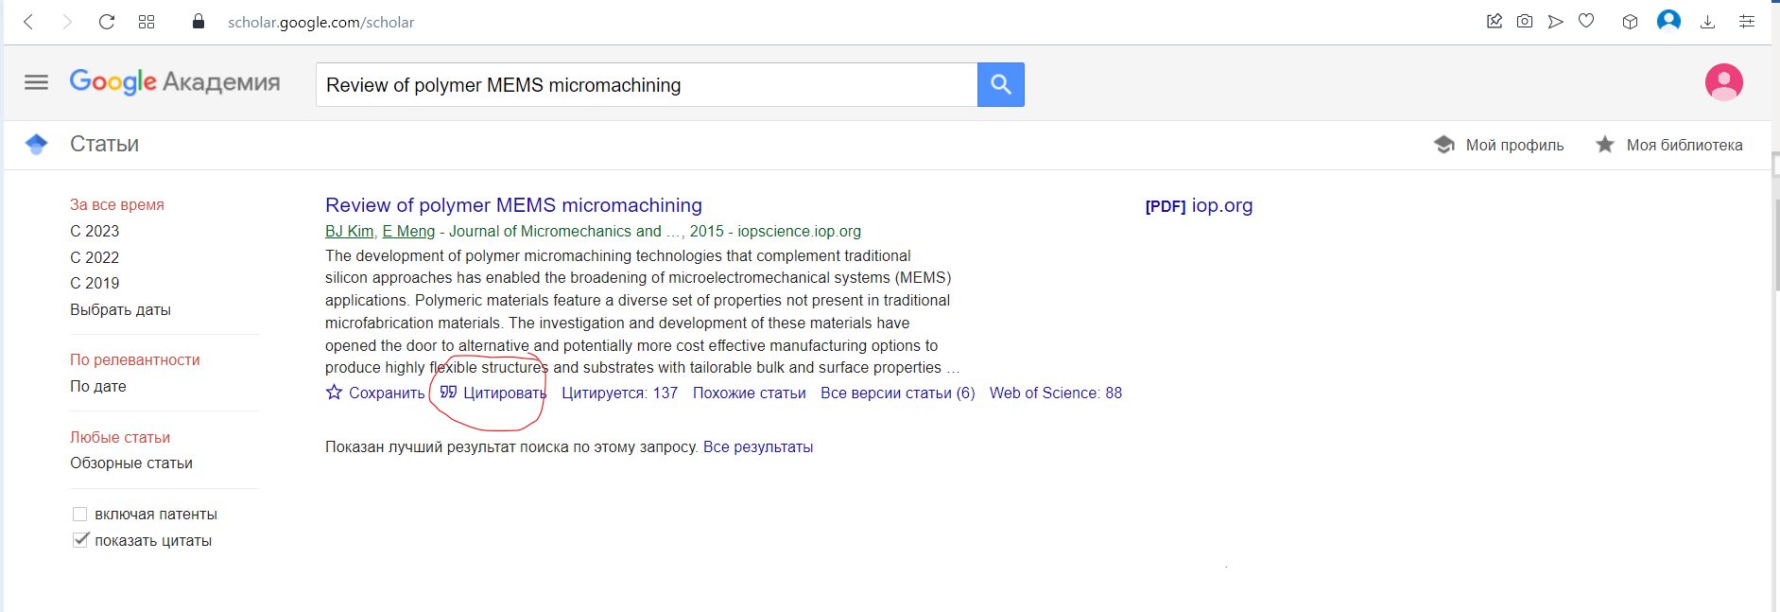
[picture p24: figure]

3. В появившемся окне видим ссылку по ГОСТУ, радуемся и копируем ее в список литературы

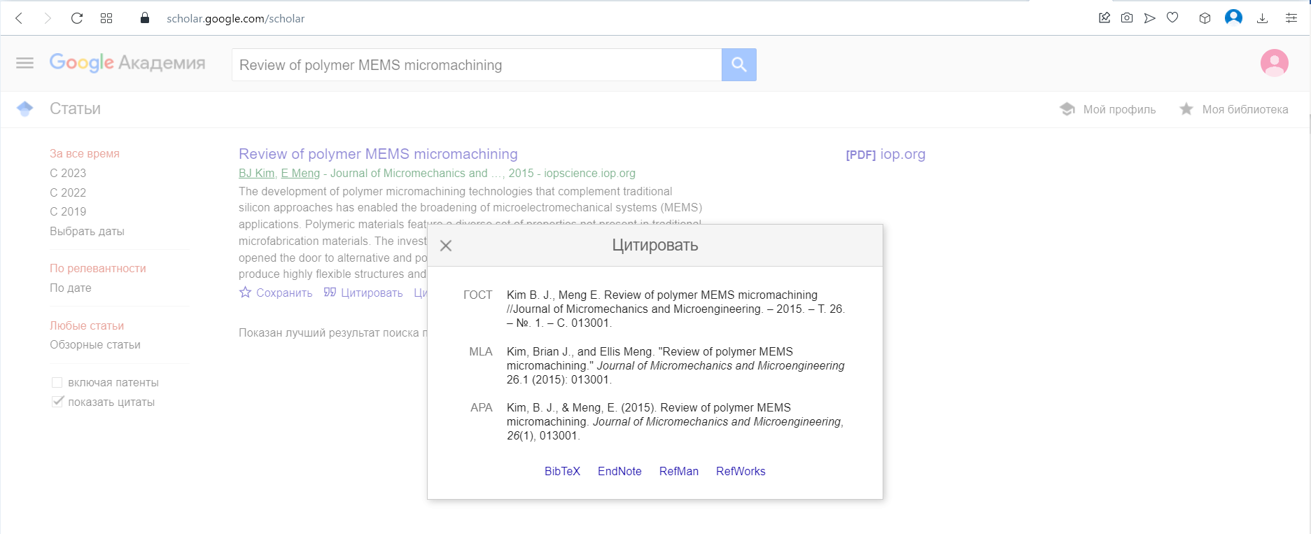
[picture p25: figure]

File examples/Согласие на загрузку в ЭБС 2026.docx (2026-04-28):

Заведующему кафедрой

МНЭ

Комкову О.С.

Я, _________________________________________,

студент группы 228Х,

даю согласие на размещение моей выпускной квалификационной работы на тему:

«______________________________________________________________»

в электронно-библиотечной системе СПбГЭТУ «ЛЭТИ».

Изъятию перед размещением подлежат следующие разделы ВКР:

Разделы ВКР | Причина изъятия

Дата __________________ Подпись

Согласовано:

Руководитель ВКР ___________________________________

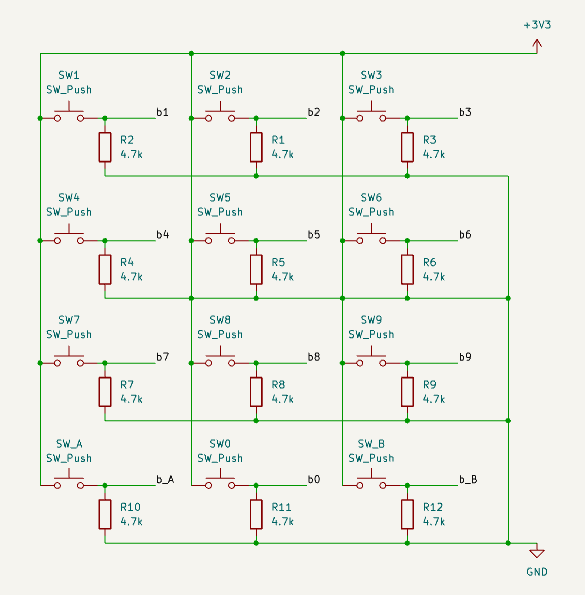
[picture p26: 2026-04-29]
images/schematics/buttons_schematics.png

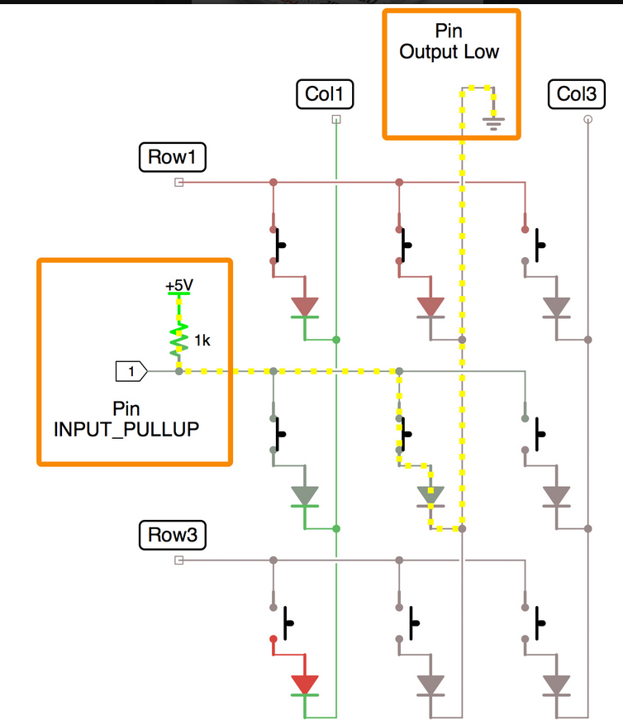
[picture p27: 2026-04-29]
images/schematics/4x3_matrix_schematics.png

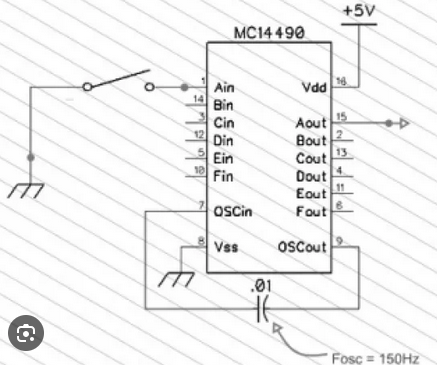
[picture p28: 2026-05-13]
images/schematics/mc14490_application.png

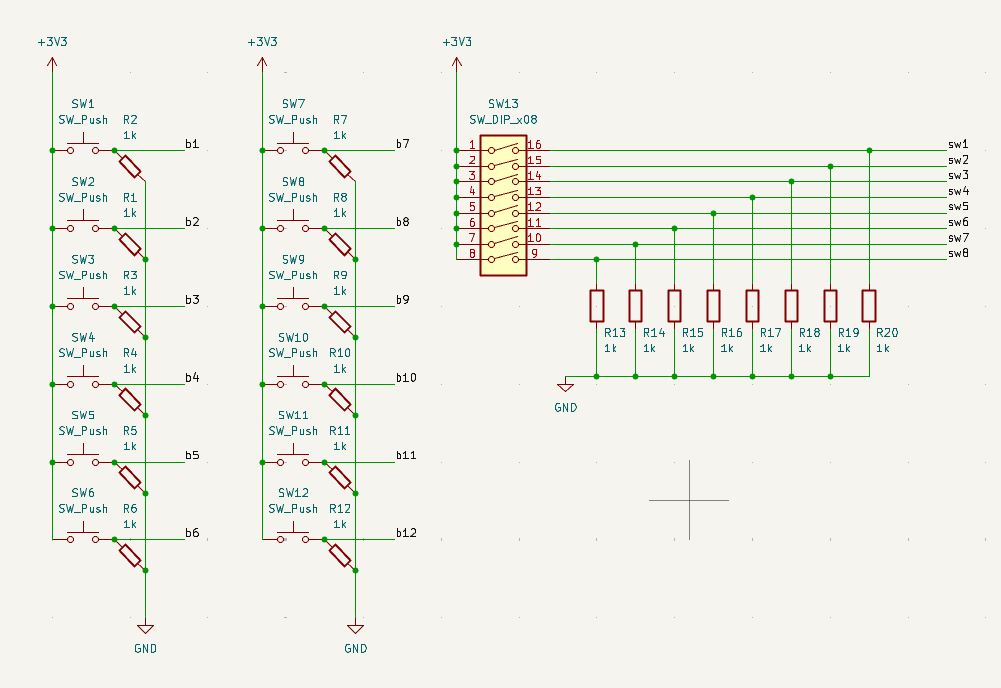
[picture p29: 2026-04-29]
images/schematics/simple_buttons_schematics.png

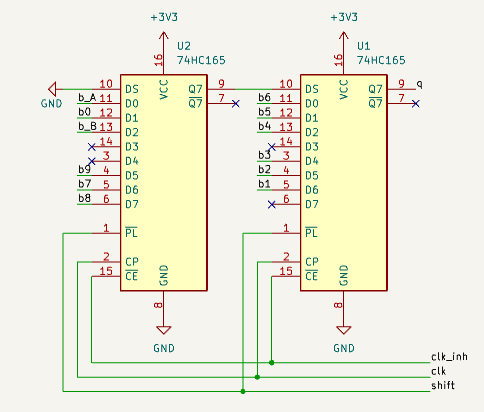
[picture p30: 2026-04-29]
images/schematics/74hc165_schematics.png

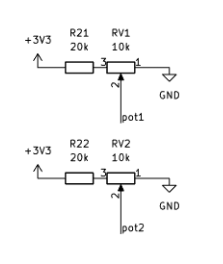
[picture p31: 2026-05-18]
images/schematics/pots.png

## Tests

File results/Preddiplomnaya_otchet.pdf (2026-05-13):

МИНОБРНАУКИ РОССИИ

САНКТ-ПЕТЕРБУРГСКИЙ ГОСУДАРСТВЕННЫЙ ЭЛЕКТРОТЕХНИЧЕСКИЙ УНИВЕРСИТЕТ «ЛЭТИ» ИМ. В.И. УЛЬЯНОВА (ЛЕНИНА) Кафедра ВТ

ОТЧЕТ
по преддипломной практике
Тема: Средства пользовательского ввода для лабораторного макета микроконтроллера
Студент гр. 2307 | Буянов М.Ю.
Руководитель к.т.н., доцент | Бондаренко П.Н.

Санкт-Петербург
2026

ЗАДАНИЕ
НА ПРЕДДИПЛОМНУЮ ПРАКТИКУ

Студент Буянов М.Ю.
Группа 2307
Тема практики: Средства пользовательского ввода для лабораторного макета микроконтроллера

Задание на практику:
В период производственной практики выполняется работа над аналитической частью выпускной квалификационной работы, посвященной разработке средств пользовательского ввода для лабораторного макета микроконтроллера MIK32 АМУР.

Основной задачей практики является изучение предметной области и
обоснование | необходимости | создания | такого | макета. | Для | этого
рассматривается | назначение | лабораторных | стендов | при | обучении
микроконтроллерным системам, определяется роль органов пользовательского ввода в проведении учебных и исследовательских работ, а также анализируются типы входных сигналов, с которыми должен работать микроконтроллер.

В ходе практики проводится обзор существующих аппаратных решений: отладочных плат на базе MIK32, распространенных плат на других микроконтроллерах и готовых учебных лабораторных стендов. При сравнении учитываются состав встроенных органов управления, стоимость, доступность, удобство применения в учебной аудитории, возможность подключения внешних устройств и пригодность для изучения разных способов ввода данных.

На основе проведенного анализа выявляется недостаток существующих решений: доступные отладочные платы, как правило, имеют ограниченный набор встроенных средств ввода, а готовые лабораторные стенды отличаются высокой стоимостью и не ориентированы на использование микроконтроллера
MIK32 | АМУР. | Поэтому | отдельно | формулируются | требования | к
разрабатываемому модулю, включая наличие кнопок, переключателей, клавиатуры, энкодера, аналоговых регуляторов и устройств, работающих по цифровым интерфейсам.

Результатом практики является подготовка первой главы ВКР, в которой представлены анализ предметной области, обзор существующих решений, классификация средств пользовательского ввода, требования к лабораторному макету и постановка задачи дальнейшей разработки.

Сроки прохождения практики: 06.04.2026 – 14.05.2026

Дата сдачи отчета:

Дата защиты отчета:

Студент | Буянов М.Ю.
Руководитель к.т.н., доцент | Бондаренко П.Н.

АННОТАЦИЯ

В рамках преддипломной практики была подготовлена аналитическая база для выпускной квалификационной работы, посвящённой разработке средств пользовательского ввода для лабораторного макета на основе микроконтроллера MIK32 АМУР. Рассмотрено назначение учебных лабораторных макетов при изучении микроконтроллерных систем, а также показана роль физических органов управления в отработке навыков работы с цифровыми, аналоговыми и импульсными входными сигналами.

В ходе работы были изучены доступные аппаратные решения: отладочные платы на базе MIK32, распространённые платы с другими микроконтроллерами и готовые учебные стенды. Анализ показал, что существующие платы обычно содержат минимальное количество встроенных органов ввода, а полноценные лабораторные стенды имеют высокую стоимость и не рассчитаны на использование MIK32 АМУР. С учётом этих ограничений определены требования к разрабатываемому макету, включая наличие нескольких типов устройств ввода, удобство эксплуатации, возможность отключения отдельных узлов, доступность элементной базы и рациональное использование выводов микроконтроллера.

По результатам практики сформировано содержание дальнейших этапов ВКР: выбор схемотехнических решений, проектирование аппаратного модуля пользовательского ввода, подготовка программных примеров для MIK32, изготовление макета и экспериментальная проверка его работы

SUMMARY

As part of the pre-graduation internship, an analytical foundation was prepared for the graduation thesis devoted to the development of user input devices for a laboratory prototype based on the MIK32 AMUR microcontroller. The purpose of educational laboratory prototypes in the study of microcontroller systems was examined, and the role of physical controls in practicing skills related to digital, analog, and pulse input signals was demonstrated.

During the work, available hardware solutions were studied, including MIK32-based development boards, widely used boards with other microcontrollers, and ready-made educational laboratory stands. The analysis showed that existing development boards usually provide only a minimal set of built-in input controls, while full-featured laboratory stands are expensive and are not designed for use with the MIK32 AMUR microcontroller. Taking these limitations into account, the requirements for the developed prototype were defined, including the presence of several types of input devices, ease of operation, the ability to disconnect individual units, availability of components, and efficient use of microcontroller pins.

Based on the results of the internship, the content of the following stages of the graduation thesis was outlined: selection of circuit design solutions, design of the hardware user input module, preparation of software examples for MIK32, fabrication of the prototype, and experimental verification of its operation.

ВВЕДЕНИЕ

Микроконтроллерные системы применяются в измерительной технике, промышленной автоматике, бытовых устройствах и средствах связи. При изучении таких систем важно не только освоить программирование микроконтроллера, но и получить практические навыки работы с внешними сигналами. Для этого в учебном процессе используются лабораторные макеты, позволяющие подключать органы управления, наблюдать реакцию программы и исследовать работу периферийных блоков микроконтроллера.

Одной из важных частей лабораторного макета являются средства пользовательского ввода. К ним относятся кнопки, переключатели, клавиатуры, энкодеры, потенциометры и другие устройства, с помощью которых пользователь формирует дискретные, аналоговые или импульсные сигналы. Работа с такими устройствами позволяет изучать настройку портов ввода-вывода, обработку дребезга контактов, использование прерываний, таймеров, аналого-цифрового преобразователя и интерфейсов обмена. Поэтому наличие удобного набора средств ввода повышает наглядность лабораторных работ и сокращает время, затрачиваемое на подготовку внешних схем.

В настоящее время существует большое количество отладочных плат и учебных стендов для микроконтроллеров. Однако большинство доступных плат содержит только минимальный набор встроенных органов управления, например одну или две кнопки и несколько светодиодов. Для выполнения лабораторных работ с клавиатурой, переключателями, аналоговыми регуляторами или энкодером требуется подключать дополнительные модули и собирать схемы на макетной плате. Готовые профессиональные стенды, напротив, часто обладают широкими функциональными возможностями, но имеют высокую стоимость и обычно ориентированы на другие микроконтроллерные платформы.

Отдельный интерес представляет применение отечественного микроконтроллера MIK32 АМУР. Он построен на архитектуре RISC-V и может использоваться как основа учебного макета для изучения современных встраиваемых систем. При этом для MIK32 ограничено количество готовых лабораторных решений и примеров программного обеспечения, связанных с обработкой пользовательского ввода. Это делает актуальной разработку собственного модуля средств ввода, который может использоваться в составе лабораторного макета и обеспечивать работу с несколькими типами входных сигналов.

Целью данной работы является разработка средств пользовательского ввода для лабораторного макета микроконтроллера MIK32 АМУР.

Объектом работы является лабораторный макет микроконтроллерной системы на базе MIK32 АМУР. Предметом разработки являются аппаратные и программные средства пользовательского ввода, предназначенные для формирования и обработки входных сигналов в учебных лабораторных работах.

Для достижения поставленной цели необходимо решить следующие задачи:

1. Рассмотреть роль пользовательского ввода в лабораторных макетах микроконтроллерных систем.
2. Проанализировать существующие отладочные платы и учебные стенды,
которые | могут | применяться | при | обучении | работе | с
микроконтроллерами.
3. Сформулировать | требования | к | разрабатываемому | модулю
пользовательского ввода.
4. Выбрать состав устройств ввода, обеспечивающий работу с дискретными, аналоговыми и импульсными сигналами.

5. Разработать схемотехнические решения для подключения кнопок, переключателей, клавиатуры, энкодера и аналоговых регуляторов к микроконтроллеру.
6. Подготовить программные алгоритмы для обработки сигналов от выбранных устройств ввода.
7. Провести | экспериментальную | проверку | работоспособности
разработанных решений.

В первой главе проводится анализ существующих лабораторных макетов, отладочных плат и учебных стендов, формулируются требования к разрабатываемому устройству и обосновывается актуальность работы. Во второй главе рассматриваются способы подключения и программной обработки кнопок, клавиатуры и рычажковых переключателей. В третьей главе описываются решения для работы с поворотным энкодером и аналоговыми ручками вращения. В четвертой главе рассматриваются вопросы безопасности при изготовлении и эксплуатации лабораторного макета. В заключении приводятся основные результаты работы.

### 1. Анализ существующих лабораторных макетов и постановка

задачи разработки

Данная глава посвящена постановке задачи разработки лабораторного макета пользовательского ввода для микроконтроллера MIK32 АМУР. В главе
рассматривается | роль | пользовательского | ввода | в | учебных
микроконтроллерных системах, приводится классификация устройств ввода и формулируются требования к лабораторному макету. Далее анализируются особенности применения MIK32 АМУР, доступные отладочные платы на его основе, распространенные платы на других микроконтроллерах и готовые учебные стенды. По результатам сравнения обосновывается актуальность разработки собственного модуля ввода, сочетающего кнопки, переключатели, клавиатуру, энкодер и аналоговые регуляторы с программными алгоритмами их обработки.

### 1.1 Роль лабораторного макета в обучении работе с микроконтроллерами

Лабораторные макеты микроконтроллеров применяются для изучения принципов работы цифровых устройств, периферийных модулей и программного обеспечения встраиваемых систем. В отличие от готового бытового устройства, учебный макет должен позволять быстро изменять режимы работы, проверять отдельные функции программы и наблюдать реакцию микроконтроллера на внешние воздействия.
Средства пользовательского ввода в таком макете выполняют несколько задач:
1. Формирование команд управления программой.
2. Задание режимов работы устройства.
3. Имитация внешних дискретных и аналоговых сигналов.
4. Проверка работы GPIO, АЦП, таймеров, прерываний и интерфейсов обмена.
5. Отладка алгоритмов обработки событий пользователя.

К средствам ввода относятся кнопки, переключатели, энкодеры, потенциометры и клавиатурные блоки. Эти устройства позволяют пользователю взаимодействовать с микроконтроллером без подключения сложного внешнего оборудования. Для учебного стенда это особенно важно, так как обучающийся должен видеть связь между физическим действием, электрическим сигналом и программной реакцией.
Модуль пользовательского ввода должен быть достаточно наглядным и надежным. Нажатие кнопки или изменение положения переключателя должны приводить к предсказуемому изменению входного сигнала. Кроме того, модуль не должен занимать слишком много выводов микроконтроллера, так как в лабораторном макете часть выводов требуется для других периферийных устройств. Поэтому при разработке необходимо учитывать не только удобство пользователя, но и ограничения аппаратной платформы. Если на плате отсутствуют встроенные органы ввода, студент вынужден каждый раз собирать внешнюю схему на макетной плате. Такой подход полезен при изучении схемотехники, но он увеличивает время подготовки лабораторной работы, повышает вероятность ошибок подключения и затрудняет массовое использование макета в учебной аудитории. Поэтому для лабораторного стенда важно иметь готовый, повторяемый и надежный модуль пользовательского ввода.

### 1.2 Классификация устройств пользовательского ввода

Устройства пользовательского ввода можно классифицировать по характеру формируемого сигнала и по способу его обработки
микроконтроллером. | Для | микроконтроллерных | систем | наиболее
распространены дискретные, аналоговые, импульсные и интерфейсные устройства ввода. В учебном макете целесообразно использовать наиболее простые представители этих групп, так как они позволяют изучить базовый принцип работы без лишней схемотехнической сложности.

Дискретные устройства формируют один из двух логических уровней. К ним относятся тактовые кнопки, рычажковые переключатели, тумблеры, герконы, концевые выключатели, микропереключатели, датчики открытия, простые датчики уровня с релейным выходом, а также клавиатуры, состоящие из набора кнопок. Тактовая кнопка используется для кратковременного воздействия: пользователь нажимает ее, программа фиксирует событие, после отпускания контакт возвращается в исходное состояние. Переключатель, в отличие от кнопки, задает устойчивое состояние и может использоваться для выбора режима работы.
Наиболее простыми представителями дискретного ввода являются кнопка и переключатель. Если микроконтроллер корректно считывает состояние кнопки, обрабатывает изменение уровня и подавляет дребезг контактов, то тот же принцип может быть применен к концевому выключателю, геркону или датчику с дискретным выходом. Поэтому в лабораторном макете достаточно использовать кнопки и рычажковые переключатели: они позволяют изучить базовую обработку логических уровней, а более сложные дискретные устройства отличаются в основном конструктивным исполнением.
Клавиатура представляет собой набор кнопок, объединенных в один блок. Она может подключаться как набор независимых кнопок либо как матрица строк и столбцов. К клавиатурным устройствам можно отнести цифровые панели 3x4 и 4x4, кнопочные панели управления, мембранные клавиатуры и наборы функциональных клавиш на приборных панелях. Для лабораторного макета клавиатура удобна тем, что позволяет вводить несколько команд при относительно компактном расположении элементов. При этом с точки зрения микроконтроллера клавиатура остается развитием дискретного ввода: программа считывает набор логических состояний и определяет, какая кнопка нажата.
В качестве базового клавиатурного устройства в работе используется клавиатура 4x3. Она достаточно проста по устройству, но позволяет рассмотреть важную для лабораторного макета задачу: считывание нескольких кнопок при ограниченном числе выводов микроконтроллера. Если программа корректно обрабатывает такую клавиатуру, то те же принципы можно применить к панели 4x4, мембранной клавиатуре или набору функциональных клавиш. Отличие будет заключаться в числе строк и столбцов, способе монтажа и количестве доступных команд, но базовый алгоритм опроса останется тем же.
Аналоговые устройства ввода формируют непрерывно изменяющееся напряжение. К ним относятся потенциометры, аналоговые джойстики, слайдеры, педали управления, датчики положения, фоторезисторы, терморезисторы, аналоговые датчики давления, датчики освещенности и другие устройства, выходной сигнал которых может быть измерен АЦП. В лабораторных макетах для изучения аналогового ввода часто применяются потенциометры, так как они просты, дешевы и позволяют вручную задавать любое значение в пределах допустимого диапазона напряжений. Потенциометр выбран как базовый аналоговый элемент, потому что он непосредственно показывает принцип работы АЦП: изменение положения ручки приводит к изменению напряжения, а программа получает соответствующее цифровое значение. Если микроконтроллер корректно считывает сигнал с потенциометра, масштабирует его и фильтрует шумы, то аналогичным образом можно обрабатывать сигнал с аналогового джойстика, датчика положения или другого аналогового датчика. Например, джойстик обычно содержит два потенциометра по осям X и Y и отдельную кнопку, поэтому его обработка сводится к считыванию двух аналоговых каналов и одного дискретного входа. Поэтому для базового лабораторного макета достаточно потенциометра: он покрывает основной принцип аналогового ввода без усложнения конструкции.
Импульсные устройства ввода формируют последовательность переходов между логическими уровнями. К ним относятся механические поворотные энкодеры, оптические энкодеры, магнитные энкодеры с импульсным выходом, датчики оборотов, тахометрические датчики и датчики с квадратурными выходами. Наиболее характерным и доступным примером является поворотный энкодер. При вращении энкодера на его выходах появляются импульсы, по которым программа определяет направление и количество шагов поворота. Энкодер удобен для изменения числовых параметров, выбора пунктов меню и плавного управления значениями без ограничения полного угла поворота.

Механический поворотный энкодер выбран как базовый представитель импульсного ввода. Если программа умеет считывать два квадратурных сигнала, определять направление вращения, подсчитывать шаги и отбрасывать некорректные переходы, то эти же принципы применимы к более сложным оптическим и магнитным энкодерам. Отличие таких устройств обычно заключается в конструкции, разрешении, скорости работы и качестве выходных сигналов, но базовая программная задача остается той же: обработать последовательность импульсов.
Отдельную группу составляют сенсорные и интерфейсные устройства ввода. К ним можно отнести емкостные сенсорные кнопки, сенсорные панели, модули клавиатурных контроллеров, RFID-считыватели, модули с датчиками жестов, цифровые датчики положения и другие устройства, передающие данные по I2C, SPI, UART или USB. Такие устройства удобны в прикладных проектах, однако они скрывают часть физических процессов внутри готового модуля и требуют изучения конкретного протокола обмена. Интерфейсными устройствами ввода можно назвать более сложные модули, которые не выдают на микроконтроллер отдельный логический или аналоговый сигнал, а передают готовые данные по протоколу обмена. К таким устройствам относятся клавиатурные контроллеры по I2C, сенсорные панели, RFID- и NFC-считыватели, цифровые джойстики, трекболы, модули распознавания жестов, цифровые датчики положения, датчики расстояния с цифровым выходом, USB HID-устройства и готовые панели оператора. В этом случае микроконтроллер должен не только получить электрический сигнал, но и настроить интерфейс, передать команду, принять пакет данных и правильно интерпретировать его содержимое.

Базовым случаем для таких устройств является работа с простым внешним модулем по SPI, I2C или UART. Например, если микроконтроллер умеет обмениваться данными с простым регистром или контроллером по SPI, то в дальнейшем тот же общий подход можно использовать для более сложного модуля: различаться будут формат команд, длина пакетов и правила обмена.
В данной работе основной акцент сделан на простых и наглядных устройствах ввода: кнопках, переключателях, клавиатуре, потенциометрах и поворотном энкодере. Такой выбор позволяет изучить основные типы сигналов, с которыми сталкивается микроконтроллер: логический уровень, набор логических уровней, аналоговое напряжение и импульсную последовательность. После освоения этих базовых случаев можно переходить к более сложным устройствам, так как они в большинстве случаев являются комбинацией тех же принципов.

### 1.3 Требования к лабораторному макету пользовательского ввода

Лабораторный макет пользовательского ввода должен быть пригоден не только для демонстрации отдельных схем, но и для регулярного применения в учебном процессе. Поэтому к нему предъявляются требования, связанные с составом устройств, стоимостью, удобством эксплуатации, использованием ресурсов микроконтроллера и возможностью расширения.
Основные требования к такому макету можно сформулировать следующим образом:
1. Наличие основных типов устройств ввода. Макет должен содержать дискретные органы управления, например кнопки и переключатели, клавиатурный блок, аналоговые регуляторы и импульсное устройство ввода, например поворотный энкодер. Такой состав позволяет
выполнять | лабораторные | работы по всем базовым видам
пользовательского ввода: считыванию логических уровней, опросу группы кнопок, обработке аналогового напряжения и анализу последовательности импульсов.
2. Умеренная стоимость. Учебный макет должен быть доступен для изготовления в нескольких экземплярах, так как лабораторное оборудование обычно используется не одним студентом, а учебной группой. Слишком дорогой стенд затрудняет тиражирование и ремонт, а также делает невозможным самостоятельное повторение работы вне лаборатории.
3. Доступность элементной базы. При разработке необходимо использовать распространенные компоненты и избегать избыточно сложных узлов, если их функции можно показать на более простых элементах. Это упрощает изготовление, ремонт и повторение макета.
4. Экономное использование выводов микроконтроллера. В лабораторном макете выводы GPIO нужны не только для пользовательского ввода, но и для интерфейсов связи, отладки, индикации, измерений и подключения внешних модулей. Поэтому макет должен позволять сравнивать разные способы подключения: прямое подключение, матричное подключение, использование сдвиговых регистров или других расширителей ввода.
5. Возможность отключения отдельных устройств ввода. В учебной практике один и тот же вывод может потребоваться в разных лабораторных работах: в одной работе он используется для кнопки, в другой - для SPI, UART, АЦП или внешнего модуля. Поэтому желательно предусмотреть перемычки, разъемы, переключатели или другие средства разрыва соединений. Это позволяет временно отключить клавиатуру, энкодер или аналоговый регулятор и использовать соответствующие линии микроконтроллера для других задач без демонтажа элементов.
6. Удобство наблюдения и проверки сигналов. Основные линии ввода желательно вывести на контрольные точки или разъемы, к которым можно подключить осциллограф, логический анализатор или мультиметр. Это особенно важно при изучении дребезга контактов, сканирования клавиатуры, работы энкодера и изменения аналогового напряжения.
7. Электрическая надежность и защита входов. Пользовательские элементы управления активно используются во время занятий, поэтому схема должна быть устойчива к частым нажатиям, ошибкам подключения и кратковременным переходным процессам. Для этого необходимо учитывать подтягивающие резисторы, ограничение токов, защиту от неопределенных состояний входов и согласование уровней с напряжением питания микроконтроллера.
8. Эргономика и однозначность использования. Органы управления должны быть расположены так, чтобы студент мог быстро понять их назначение. Кнопки, переключатели, энкодер и аналоговые ручки должны иметь понятные обозначения, а их состояние должно легко считываться визуально.
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

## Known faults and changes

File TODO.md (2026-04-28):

## TODO
- проверить самодельную схему борьбы с дребезгом
- проверить готовое решение
- принести в уник и написать тест для всех устройств ввода
- подключить 74HC165 к SPI через резистор
- сравнить bit-banging и SPI для 74HC165

## Bookmarks
- [toolchain](https://habr.com/ru/articles/854050/)
- [uploader](https://docs.mikron.ru/wiki/dev-tools/soft/uploader.html)
- [debouncer IC](https://www.chipdip.ru/product/mc14490dwg-ic-digital-contact-bounce-on-semiconductor-8051233161)

## rev. 1
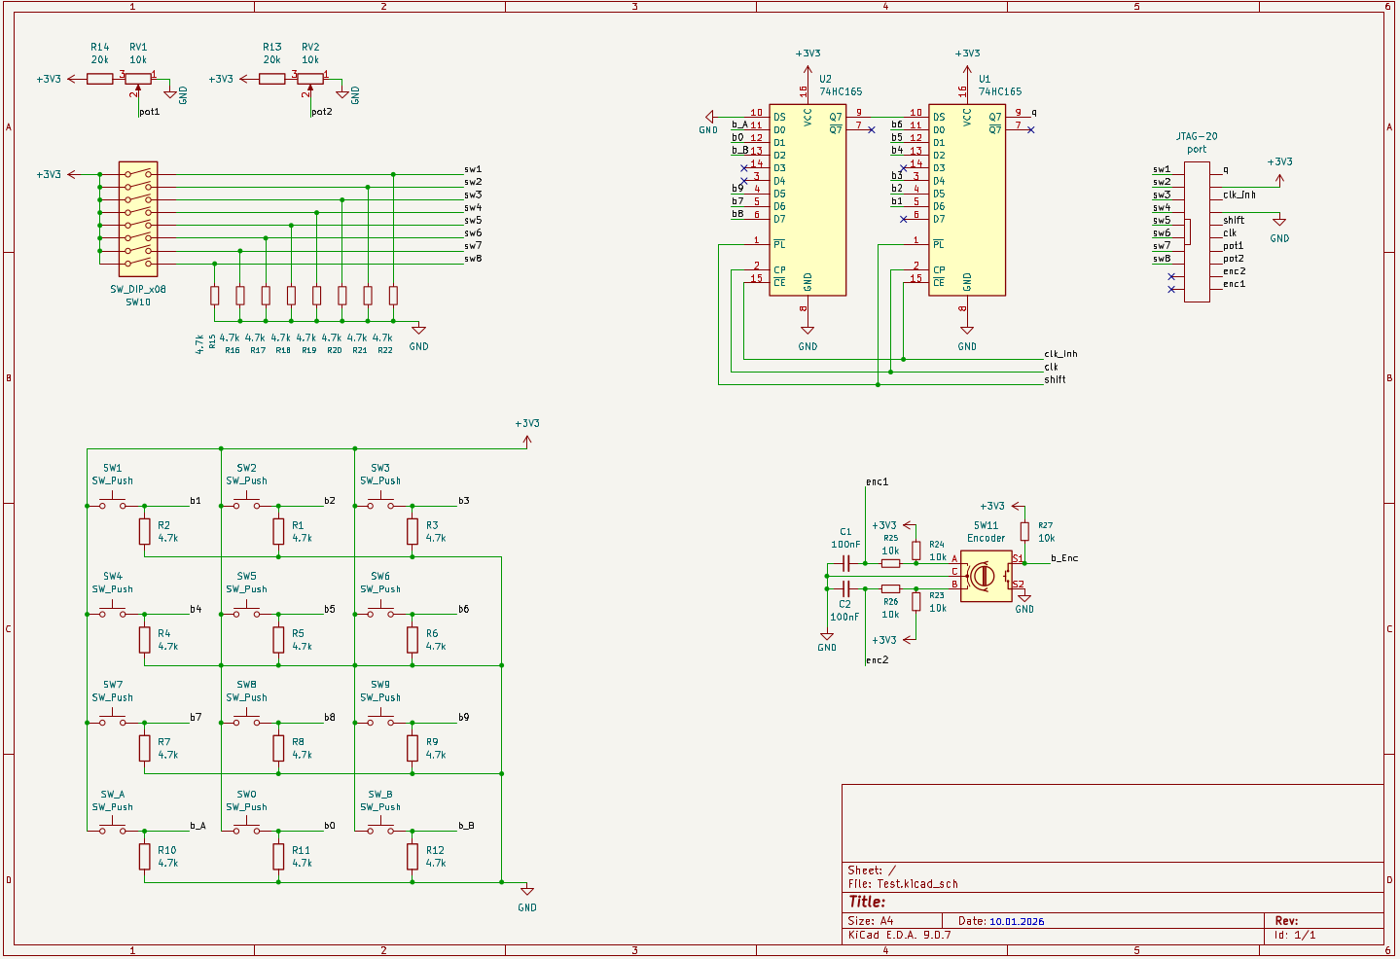
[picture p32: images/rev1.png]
Schematics


### Особенности
- 12 кнопок через 2 74HC165
- готовый китайский модуль энкодера
- 8 рычажковых переключателей подключены напрямую без борьбы с дребезгом.
- 2 потенциометра от 0v до 1v1
- все устройства ввода проверены с Arduino -> все собрано верно

## Исследование условий эксплуатации
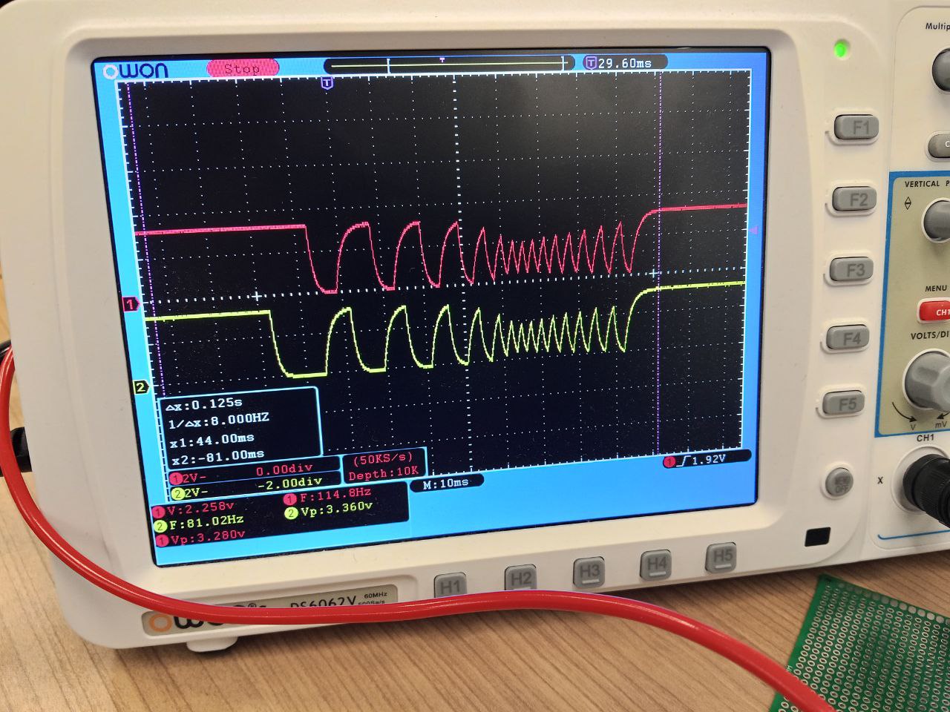
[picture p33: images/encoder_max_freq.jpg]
encoder oscillogram
Нужно исследовать как часто нажимаются кнопки, как быстро отпускаются, худшие характеристики нажатия и тд. По предварительным результатам (нужно провести более серьезный тест на нескольких людях и на разных устройствах) тактовую кнопку можно нажать не менее чем на 40 мс с периодом между нажатиями не менее 40 мс. Наибольшая частота сигнала с одного канала энкодера состовляет около 0.5 кГц (картинка ниже) . Можно заметить, что китайский модуль не расчитан на такую скорость значения, и нужно изменить характеристики фильтра.

## Защита от дребезга
Рассмотрим различные варианты защиты от дребезга контактов (кнопок и рычажковых переключателей)
### MC14490
[ссылка на чип и дип](https://www.chipdip.ru/product/mc14490dwg-ic-digital-contact-bounce-on-semiconductor-8051233161)\
Хорошо работает, не занимает дополнительных пинов и не требует дополнительного ПО, каждая схема имеет 6 каналов. Цена в районе 100 рублей за штуку (200 рублей за плату). Существует задержка до 100 мс (можно уменьшить до 10 мс поменяв конденсатор с 10 нф на 1 нф). 
### Программная фильтрация дребезга
TODO
### RC-фильтр
Требует большого количества компонентов (N x 3), но практически ничего не стоит и компоненты всегда в наличии, задержка до 10 мс, но может быть значительно меньше при хороших кнопках. Имеет смысл использовать при распайке на печатной плате, но на макетке очень тяжело будет все разместить и паять.

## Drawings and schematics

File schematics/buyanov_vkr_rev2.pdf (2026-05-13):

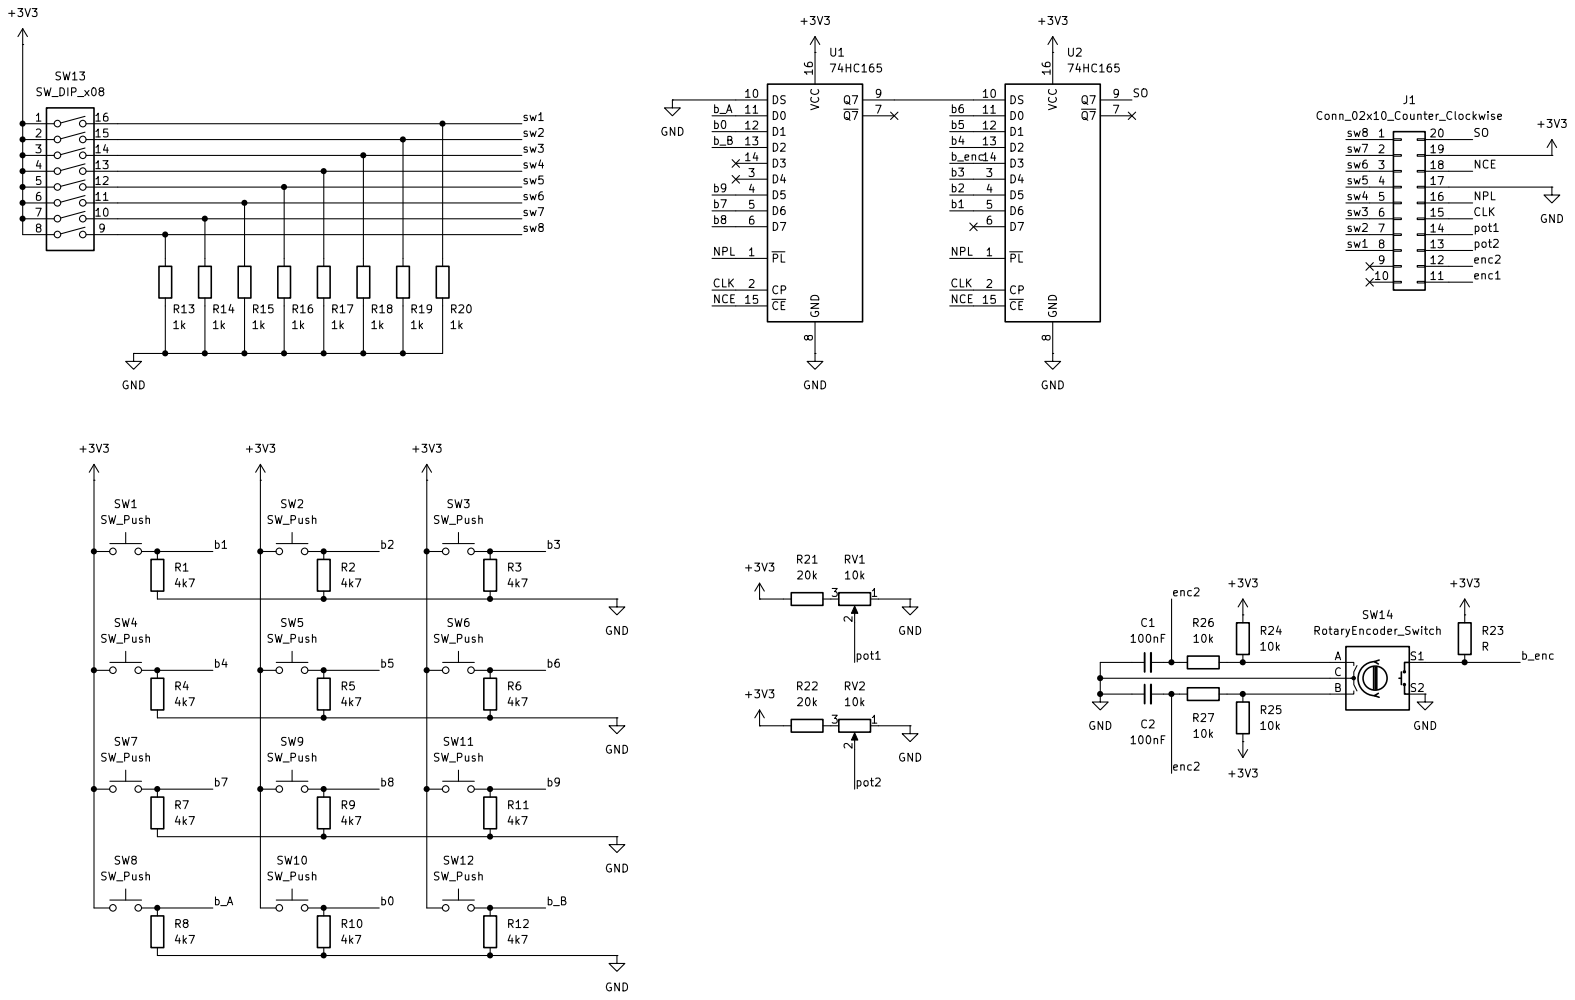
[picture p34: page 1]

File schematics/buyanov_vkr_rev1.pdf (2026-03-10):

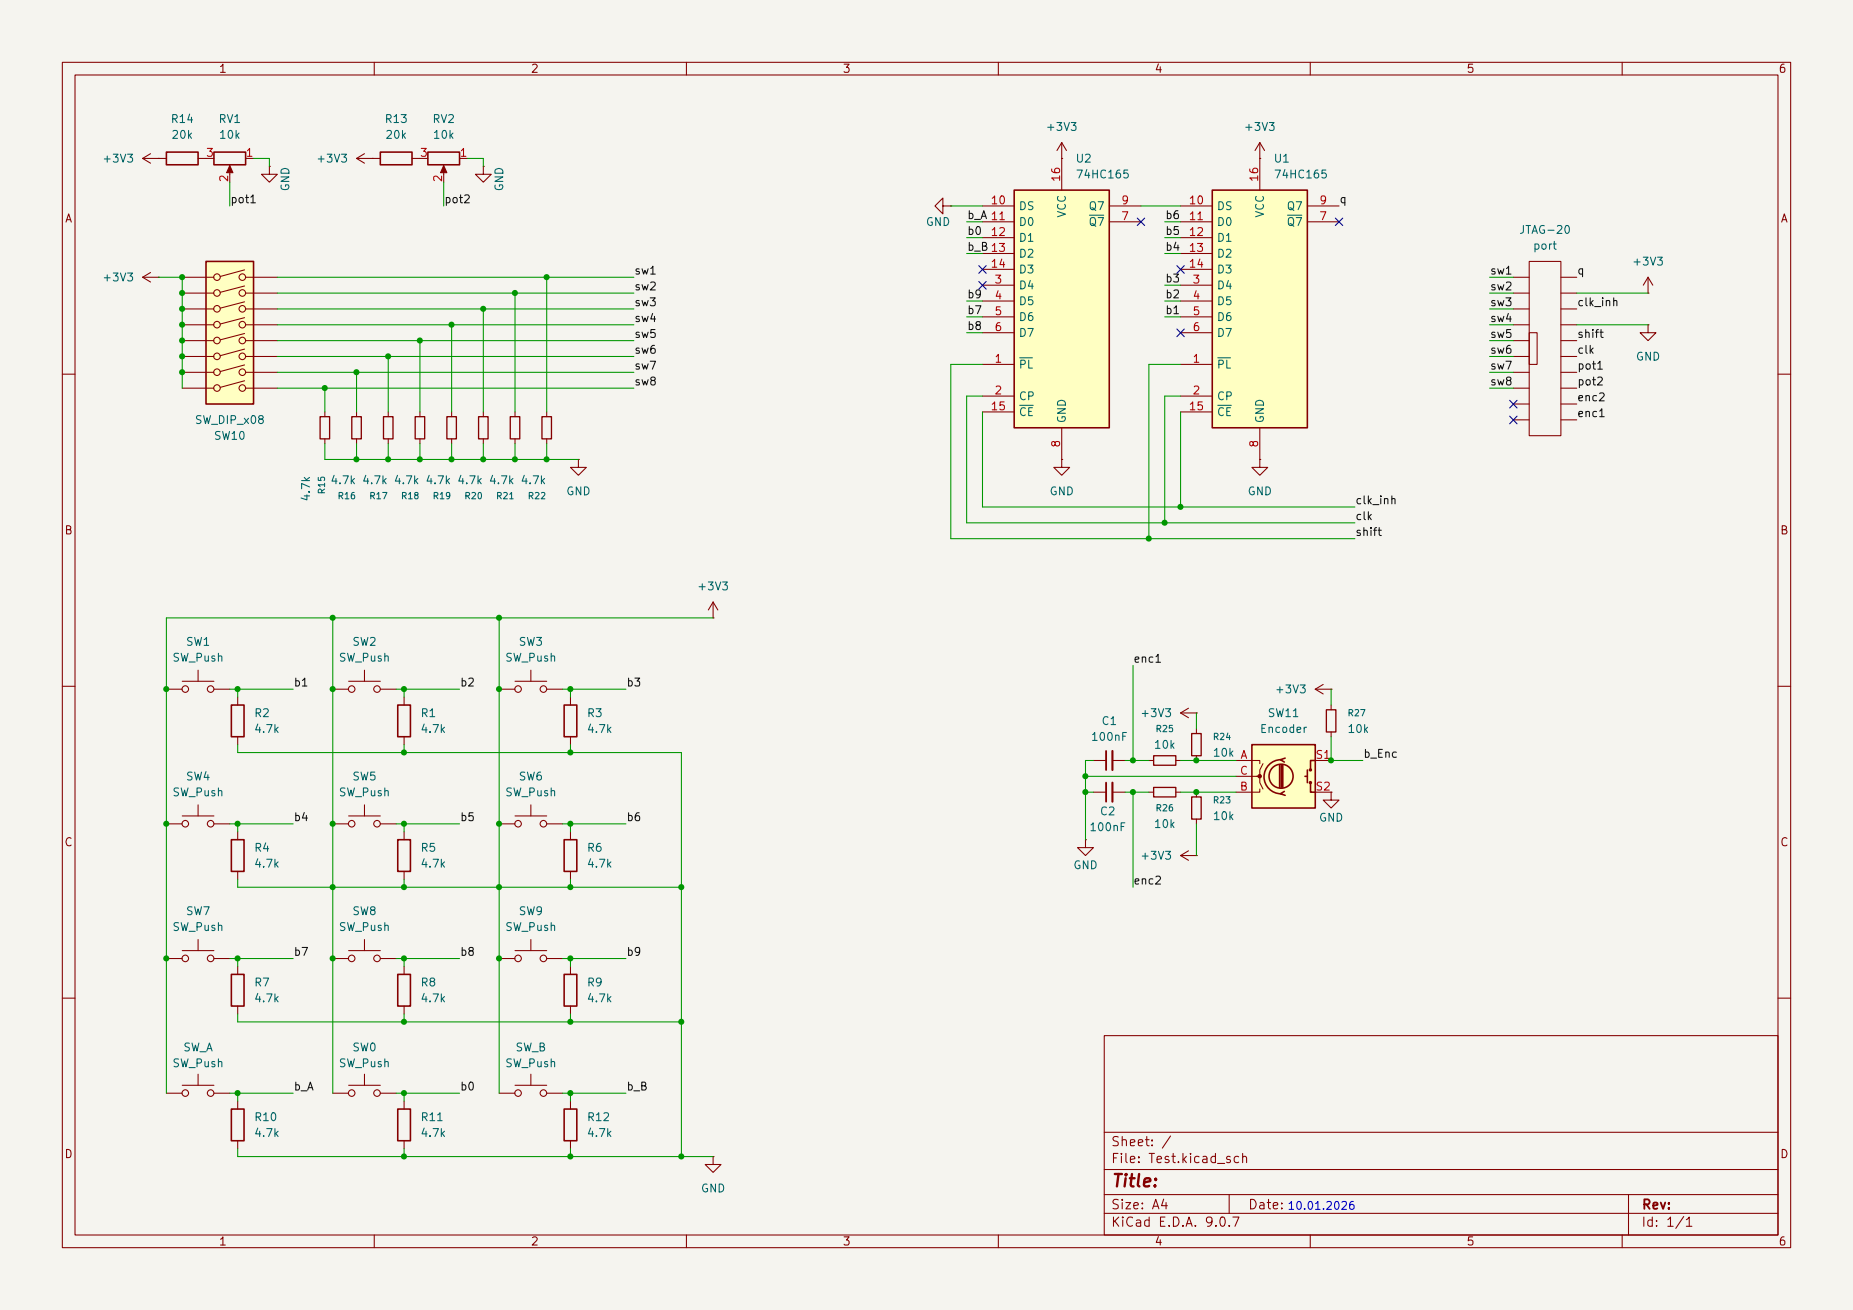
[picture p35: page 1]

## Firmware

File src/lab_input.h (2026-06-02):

/*
 * user_input.h
 *
 */

#ifndef USER_INPUT_H_
#define USER_INPUT_H_

#include <stdint.h>
#include "mik32_hal_adc.h"
#include "mik32_hal_gpio.h"
#include "mik32_hal_spi.h"

#define LI_SW1_PORT GPIO_1
#define LI_SW2_PORT GPIO_1
#define LI_SW3_PORT GPIO_1
#define LI_SW4_PORT GPIO_1
#define LI_SW5_PORT GPIO_2
#define LI_SW6_PORT GPIO_2
#define LI_SW7_PORT GPIO_1
#define LI_SW8_PORT GPIO_1

#define LI_SW1_PIN 8
#define LI_SW2_PIN 9
#define LI_SW3_PIN 1
#define LI_SW4_PIN 4
#define LI_SW5_PIN 6
#define LI_SW6_PIN 7
#define LI_SW7_PIN 3
#define LI_SW8_PIN 6

#define LI_ENC0_PORT GPIO_0
#define LI_ENC1_PORT GPIO_0

#define LI_ENC0_PIN 8
#define LI_ENC1_PIN 9

#define LI_SPI_CS SPI_CS_1

#define MIK32V2

#define LI_BTN0_BIT

// must be called at 1 kHz
void li_update();

// must be called once
void li_init();

enum LI_ButtonIndexes {
	B_0,
	B_1,
	B_2,
	B_3,
	B_4,
	B_5,
	B_6,
	B_7,
	B_8,
	B_9,
	B_A,
	B_B,
	B_ENC
};

static const uint32_t li_buttons_map[] = {
		10, // B_0
		7, // B_1
		6,
		5,
		3,
		2,
		1,
		15,
		0,
		14,
		11, // B_A
		9, // B_B
		8  // B_ENC TODO value is likely wrong
};

uint8_t li_get_button_state(enum LI_ButtonIndexes button);

static uint32_t li_update_counter			= 0;
static uint32_t li_buttons_state_bitmask	= 0; // b0, ... b9, bA, bB, bEnc
static uint32_t li_levers_state_bitmask		= 0;
static uint32_t li_pot_value_left			= 0;
static uint32_t li_pot_value_right			= 0;

static int32_t li_enc_counter				= 0;
static ADC_HandleTypeDef hadc;
static SPI_HandleTypeDef hspi;

static void li_poll_encoder() {
	static uint8_t p0 = 0, p1 = 0; // encoder last state
	uint8_t e0 = (LI_ENC0_PORT->STATE >> LI_ENC0_PIN) & 1;
	uint8_t e1 = (LI_ENC1_PORT->STATE >> LI_ENC1_PIN) & 1;

	if (p0 ^ p1 ^ e0 ^ e1) {
		(p1 ^ e0) ? li_enc_counter++ : li_enc_counter--;
		p0 = e0;
		p1 = e1;
	}

}

// https://habr.com/ru/articles/836796/
static void li_poll_potentiometers() {
	/* Получение значения с разных каналов */
	        ADC_SEL_CHANNEL(hadc.Instance, 1); // set ch1 (P1.7)
	        HAL_ADC_SINGLE(hadc.Instance); // Первое измерение для переключение на канал 0.
	        HAL_ADC_WaitValid(&hadc);

	        HAL_ADC_SINGLE_AND_SET_CH(hadc.Instance, 1); // read ch1 (P1.7), then set channel to 2
	        li_pot_value_left = HAL_ADC_WaitAndGetValue(&hadc);

	        HAL_ADC_SINGLE_AND_SET_CH(hadc.Instance, 2); // read ch2 (P0.2)
	        li_pot_value_right = HAL_ADC_WaitAndGetValue(&hadc);
}

uint8_t li_get_button_state(enum LI_ButtonIndexes button) {
	return (li_buttons_state_bitmask & (1 << button)) ? 1 : 0;
}


static void li_poll_levers() {
	li_levers_state_bitmask = 0;
	li_levers_state_bitmask |= ((LI_SW1_PORT->STATE >> LI_SW1_PIN) & 1) << 0;
	li_levers_state_bitmask |= ((LI_SW2_PORT->STATE >> LI_SW2_PIN) & 1) << 1;
	li_levers_state_bitmask |= ((LI_SW3_PORT->STATE >> LI_SW3_PIN) & 1) << 2;
	li_levers_state_bitmask |= ((LI_SW4_PORT->STATE >> LI_SW4_PIN) & 1) << 3;
	li_levers_state_bitmask |= ((LI_SW5_PORT->STATE >> LI_SW5_PIN) & 1) << 4;
	li_levers_state_bitmask |= ((LI_SW6_PORT->STATE >> LI_SW6_PIN) & 1) << 5;
	li_levers_state_bitmask |= ((LI_SW7_PORT->STATE >> LI_SW7_PIN) & 1) << 6;
	li_levers_state_bitmask |= ((LI_SW8_PORT->STATE >> LI_SW8_PIN) & 1) << 7;
}

uint32_t li_get_keyboard_bitmask() {
	return li_buttons_state_bitmask;
}

//// https://habr.com/ru/articles/832228/
static void li_poll_keyboard() {
	uint16_t data = 0;

    /* Начало передачи в ручном режиме управления CS */
    if (hspi.Init.ManualCS == SPI_MANUALCS_ON)
    {
    	HAL_SPI_Enable(&hspi);
        HAL_SPI_CS_Disable(&hspi);
    }

    /* Передача и прием данных */
    HAL_StatusTypeDef SPI_Status = HAL_SPI_Exchange(&hspi, (uint8_t*)&data, (uint8_t*)&data, 2, SPI_TIMEOUT_DEFAULT); // sending data doesnt do anything
    if (SPI_Status != HAL_OK) {
    	// ignore error
        while (1);
    }

    /* Конец передачи в ручном режиме управления CS */
    if (hspi.Init.ManualCS == SPI_MANUALCS_ON)
    {
        HAL_SPI_CS_Enable(&hspi, LI_SPI_CS);
        HAL_SPI_Disable(&hspi);
    }

    li_buttons_state_bitmask = 0;
    li_buttons_state_bitmask |= (((data >> li_buttons_map[B_0]) & 1) << B_0);
    li_buttons_state_bitmask |= (((data >> li_buttons_map[B_1]) & 1) << B_1);
    li_buttons_state_bitmask |= (((data >> li_buttons_map[B_2]) & 1) << B_2);
    li_buttons_state_bitmask |= (((data >> li_buttons_map[B_3]) & 1) << B_3);
    li_buttons_state_bitmask |= (((data >> li_buttons_map[B_4]) & 1) << B_4);
    li_buttons_state_bitmask |= (((data >> li_buttons_map[B_5]) & 1) << B_5);
    li_buttons_state_bitmask |= (((data >> li_buttons_map[B_6]) & 1) << B_6);
    li_buttons_state_bitmask |= (((data >> li_buttons_map[B_7]) & 1) << B_7);
    li_buttons_state_bitmask |= (((data >> li_buttons_map[B_8]) & 1) << B_8);
    li_buttons_state_bitmask |= (((data >> li_buttons_map[B_9]) & 1) << B_9);
    li_buttons_state_bitmask |= (((data >> li_buttons_map[B_A]) & 1) << B_A);
    li_buttons_state_bitmask |= (((data >> li_buttons_map[B_B]) & 1) << B_B);
    li_buttons_state_bitmask |= (((data >> li_buttons_map[B_ENC]) & 1) << B_ENC);
}

void li_update() {
	li_update_counter++;

	// 1 KHz
	li_poll_encoder();

	// 100 Hz
	if (li_update_counter % 10 == 0) {
		li_poll_keyboard();
	}

	// 33 Hz
	if (li_update_counter % 30 == 0) {
		// li_poll_levers();
	}

	if (li_update_counter % 10 == 0) {
		li_poll_potentiometers();
	}
}

void li_init_levers() {
		LI_SW1_PORT->DIRECTION_IN |= 1 << LI_SW1_PIN;
		LI_SW2_PORT->DIRECTION_IN |= 1 << LI_SW2_PIN;
		LI_SW3_PORT->DIRECTION_IN |= 1 << LI_SW3_PIN;
		LI_SW4_PORT->DIRECTION_IN |= 1 << LI_SW4_PIN;
		LI_SW5_PORT->DIRECTION_IN |= 1 << LI_SW5_PIN;
		LI_SW6_PORT->DIRECTION_IN |= 1 << LI_SW6_PIN;
		LI_SW7_PORT->DIRECTION_IN |= 1 << LI_SW7_PIN;
		LI_SW8_PORT->DIRECTION_IN |= 1 << LI_SW8_PIN;

		PAD_CONFIG->PORT_1_PUPD |= 1 << (LI_SW1_PIN * 2 + 1);
		PAD_CONFIG->PORT_1_PUPD |= 1 << (LI_SW2_PIN * 2 + 1);
		PAD_CONFIG->PORT_1_PUPD |= 1 << (LI_SW3_PIN * 2 + 1);
		PAD_CONFIG->PORT_1_PUPD |= 1 << (LI_SW4_PIN * 2 + 1);
		PAD_CONFIG->PORT_2_PUPD |= 1 << (LI_SW5_PIN * 2 + 1);
		PAD_CONFIG->PORT_2_PUPD |= 1 << (LI_SW6_PIN * 2 + 1);
		PAD_CONFIG->PORT_1_PUPD |= 1 << (LI_SW7_PIN * 2 + 1);
		PAD_CONFIG->PORT_1_PUPD |= 1 << (LI_SW8_PIN * 2 + 1);
}

void li_init() {
	// TODO pins should not be hardcoded but passed as config struct
	// TODO lever pin are swapped on schematics (1 to 8 instead of 8 to 1)
//	li_init_levers();

	hadc.Instance = ANALOG_REG;
	hadc.Init.Sel = ADC_CHANNEL0;
	hadc.Init.EXTRef = ADC_EXTREF_OFF;    /* Выбор источника опорного напряжения: «1» - внешний; «0» - встроенный */
	hadc.Init.EXTClb = ADC_EXTCLB_ADCREF; /* Выбор источника внешнего опорного напряжения: «1» - внешний вывод; «0» - настраиваемый ОИН */
	HAL_ADC_Init(&hadc);

	hspi.Instance = SPI_1;

	/* Режим SPI */
	hspi.Init.SPI_Mode = HAL_SPI_MODE_MASTER;

	/* Настройки */
	hspi.Init.CLKPhase = SPI_PHASE_ON;
	hspi.Init.CLKPolarity = SPI_POLARITY_HIGH;
	hspi.Init.ThresholdTX = 4;

	/* Настройки для ведущего */
	hspi.Init.BaudRateDiv = SPI_BAUDRATE_DIV256;
	hspi.Init.Decoder = SPI_DECODER_NONE;
	hspi.Init.ManualCS = SPI_MANUALCS_ON;
	hspi.Init.ChipSelect = LI_SPI_CS;

	 if (HAL_SPI_Init(&hspi) != HAL_OK)
		 while (1);

	LI_ENC0_PORT->DIRECTION_IN |= 1 << LI_ENC0_PIN;
	LI_ENC1_PORT->DIRECTION_IN |= 1 << LI_ENC1_PIN;
}

uint32_t li_get_levers_bitmask() {
	return li_levers_state_bitmask;
}

int32_t li_get_enc_counter() {
	return li_enc_counter;
}

enum LI_Pot {
	Left = 0,
	Right = 1
};

uint16_t li_get_pot_value_mv(uint8_t pot) {
	return pot ? (li_pot_value_right * 1300 / 4096) : (li_pot_value_left * 1300 / 4096);
}

void HAL_ADC_MspInit(ADC_HandleTypeDef *hadc)
{
    GPIO_InitTypeDef GPIO_InitStruct = {0};
    __HAL_PCC_ANALOG_REGS_CLK_ENABLE();

    if ((hadc->Init.EXTClb == ADC_EXTCLB_ADCREF) && (hadc->Init.EXTRef == ADC_EXTREF_ON))
    {
#ifdef MIK32V0
        GPIO_InitStruct.Pin = GPIO_PIN_10;
#endif

#ifdef MIK32V2
        GPIO_InitStruct.Pin = GPIO_PIN_11;
#endif
    }

    GPIO_InitStruct.Mode = HAL_GPIO_MODE_ANALOG;
    GPIO_InitStruct.Pull = HAL_GPIO_PULL_NONE;
    HAL_GPIO_Init(GPIO_1, &GPIO_InitStruct);

    /* Настройка выводов АЦП */
    GPIO_InitStruct.Pin = GPIO_PIN_7;
    HAL_GPIO_Init(GPIO_1, &GPIO_InitStruct);

    GPIO_InitStruct.Pin = GPIO_PIN_2;
    HAL_GPIO_Init(GPIO_0, &GPIO_InitStruct);
}

#endif /* USER_INPUT_H_ */

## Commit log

2026-04-29 2.1 to 2.7 refactor and images
    [test.kicad_pcb, test.kicad_sch]
2026-05-03 chapter 1 prototype
2026-05-07 Added printing to main.c
2026-05-13 PUBLICATION.md update
    [test.kicad_sch, test2.kicad_pcb, test2.kicad_sch]
2026-06-02 a lot of stuff
    [test.kicad_sch, test2.kicad_sch]
